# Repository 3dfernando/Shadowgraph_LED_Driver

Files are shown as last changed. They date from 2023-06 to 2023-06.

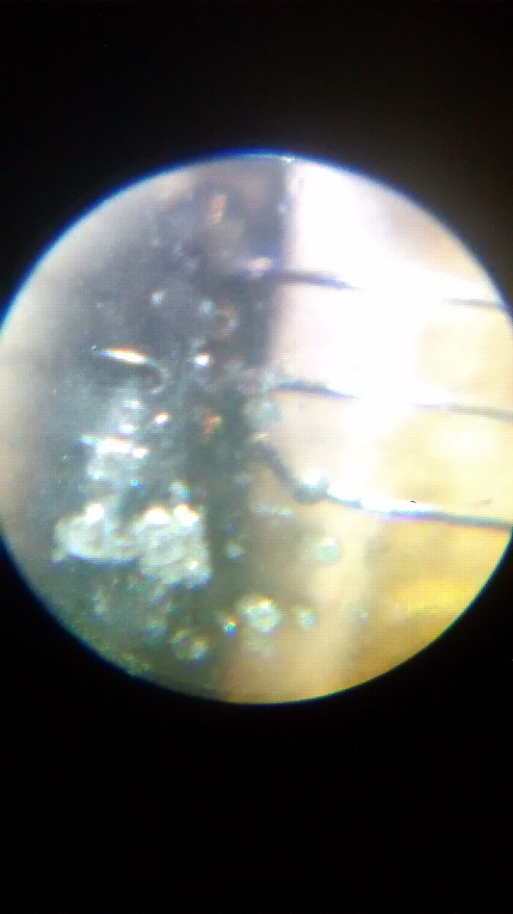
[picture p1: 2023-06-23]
Failure Pictures/IMG_20171130_173702805.jpg

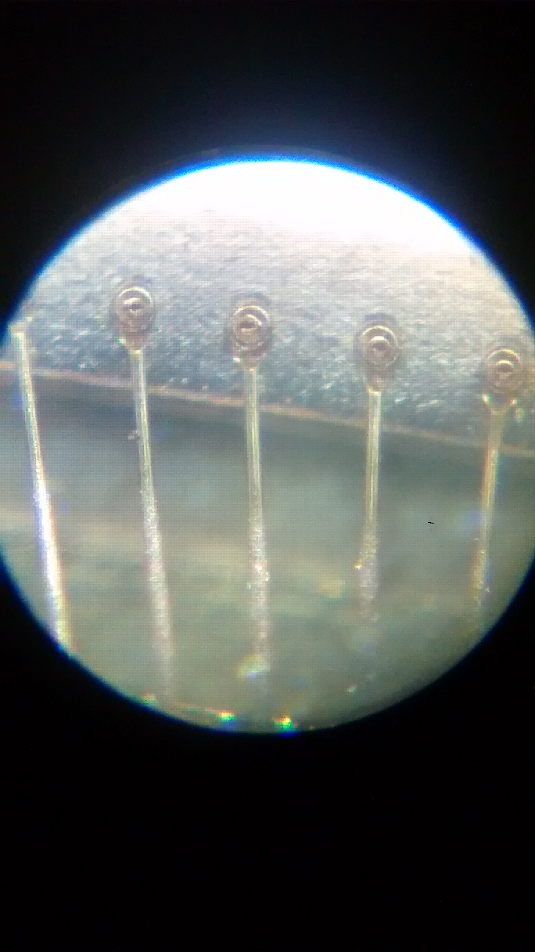
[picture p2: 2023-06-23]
Failure Pictures/IMG_20171130_174007732.jpg

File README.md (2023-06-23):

# Shadowgraph LED Driver
A simple electronic circuit board design for overdriving a pulsed LED flash for shadowgraph purposes. 

*** WARNING: This circuit overdrives an LED with up to 200A of current. COMPONENTS WILL GET BURNED! Be careful in your explorations and make sure you understand the circuit before you start messing with it! ***

# Circuit Description
The circuit schematic, provided in Circuit Diagram.pdf, is very simple. 
24V are provided to a nominally 3.8V LED through a high-power MOSFET (IRF3805) for the duration of the input pulse, which should be very short (order 10us or less) and of very low duty cycle (less than 1% recommended).

The current provided to the LED can reach 200A at full power. 200A will, however, explode the LED bond wires, rendering it useless. Since the LED is very expensive (about $100 as of 2023 for the white LED), it is not recommended to drive at max power. The LED provides a good flash at 100-120A and you should really not exceed 150A (that's where sometimes it may or may not burn depending on other conditions).

There is so much current in such a little time to run the LED that the MOSFET IRF3805 needs a driver IC to provide the inrush current of up to 8A. This obviously cannot be provided by a function generator, which is why the UCC27424 is there to convert the high impedance of the fn. generator to a low impedance required by the MOSFET gate. The UCC27424 can be destroyed if the MOSFET fails. This is because when the MOSFET fails, it can fail such that the Gate and Source terminal are shorted. In this case, the current going through the UCC driver will exceed the 8A rating and burn the IC, so both need to be replaced in this case.

To adjust the amount of current going through the LED, adjust the output voltage of the LM2596 DC-DC converter circuit. This can be done using a small screwdriver to adjust the trimmer-potentiometer in the DC-DC converter. The output voltage will range between 9 and 16V during operation, depending on the amount of current you want for the LED. 

The amount of current running through the LED can be measured with an oscilloscope by watching the voltage drop across the 0.02Ohm resistor. For 100A, for example, we have V=I*R=100A * 0.02Ohm = 2V across the resistor. Since the LED is expensive, you can connect a piece of short wire between the LED terminal connectors (i.e., generate a short circuit), in order to test the system. Once you are confident the current is about 100A or so, connect the LED and test your optics to see if the brightness is sufficient. If it isn't, you can increase the power by using the trimmer-potentiometer in the DC-DC converter, bearing in mind that at about 150A the LED, MOSFET and UCC driver will be destroyed.

Note: The LED has a small thermal mass and will heat up rather quickly if you use a high duty cycle for this driver. The average power dissipation of the LED can exceed 1200W with 1% duty cycle, meaning you will not be able to build a heat sink with acceptable specs for the LED. Best is to simply bolt the LED to a large aluminium block to provide it with thermal mass, and just not run it for too long. The LED may fail over a few minutes if it overheats.

# How to make this
1. First, download Gerbers.zip and send the Gerber files to a PCB manufacturer company.
2. Assemble the PCB according to Circuit Diagram.pdf. Make sure all components are oriented correctly! The bill of materials is provided in BOM.xlsx
3. There is an Operation Instructions.pptx file with directions and pictures on how the PCB looks like. The terminal blocks and DIP8 socket enable replacement of the components that are likely to be damaged if you don't know what you are doing. Make sure you buy extra transistors IRF3805 and UCC27424P chips, as they really can burn very easily until you understand the limitations of this device. 
4. Start testing the board, according to the instructions and warnings in "Circuit Description". Have spare parts - you will need them!

# Known operation conditions
This circuit has been successfully operated at conditions listed below:
* 500Hz, 10us pulse width, indefinitely;
* 500kHz, 0.5us pulse width, for 2-3 seconds (Pulse burst mode in a function generator);
* 10-50kHz, 1us pulse width, for ~30 seconds;
* Minimum pulse width to get any meaningful amount of light is about 100ns (See Pictures/Photodiode measurements folder);
* This circuit is not designed to operate without pulsing (i.e., continuously). Likely all components will fail due to the extremely high currents.

As you can see, this is a very tricky circuit to work with. It provides some real juice for your shadowgraphs, allowing for imaging at very high frame rates. Have fun building it!

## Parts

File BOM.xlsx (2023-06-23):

Item | Qty | Cost/ea | Total Cost | Link
1. Electronic Driver Board |  |  | $22.25
LM2596 Buck Converter, DC to DC | 1 | $1.33 | $1.33 | https://www.amazon.com/LM2596-Converter-3-0-40V-1-5-35V-Supply/dp/B0B3M91PNJ/ref=sr_1_4
UCC27424P | 1 | $1.61 | $1.61 | https://www.digikey.com/en/products/detail/texas-instruments/UCC27424P/603254
RES 22K | 2 | $0.10 | $0.20 | https://www.digikey.com/en/products/detail/yageo/CFR-12JB-52-22K/3966
RES 1.5OHM | 1 | $0.42 | $0.42 | https://www.digikey.com/en/products/detail/te-connectivity-passive-product/RR03J1R5TB/9371815
BNC CONNECTOR | 1 | $1.94 | $1.94 | https://www.digikey.com/en/products/detail/molex/0731000105/1465146
IRF3805 | 1 | $4.15 | $4.15 | https://www.digikey.com/en/products/detail/infineon-technologies/AUIRF3805/2605469
RES 0.02OHM | 1 | $0.97 | $0.97 | https://www.digikey.com/en/products/detail/riedon/MSR3-0R02F1/1641078
TERM BLK 3POS TOP ENT 5.08MM PCB | 1 | $1.86 | $1.86 | https://www.digikey.com/en/products/detail/te-connectivity-amp-connectors/282851-3/1136743
MACHINED DIP 8 SOCKET | 1 | $0.50 | $0.50 | https://www.digikey.com/en/products/detail/mill-max-manufacturing-corp/110-99-308-41-001000/32045
TERMINAL BLOCK 2 POS, SCREW TYPE, 5.08 | 3 | $0.77 | $2.31 | https://www.digikey.com/en/products/detail/cui-devices/TB004-508-02BE/10064103
1uF CAP | 1 | $1.93 | $1.93 | https://www.digikey.com/en/products/detail/avx-corporation/SR215C105KAR/7536274
330uF CAP | 1 | $0.69 | $0.69 | https://www.digikey.com/en/products/detail/illinois-capacitor/337CKS050M/5412323
Power Connector PCB Male | 1 | $0.96 | $0.96 | https://www.digikey.com/en/products/detail/w%C3%BCrth-elektronik/694108301002/5047524
Power Connector Cable Female | 1 | $1.66 | $1.66 | https://www.digikey.com/en/products/detail/cui-devices/PP3-002BH/2197312
THT Connector Female | 4 | $0.43 | $1.72 | https://www.digikey.com/en/products/detail/mill-max-manufacturing-corp/801-47-001-10-001000/7364070
2. LEDs |  |  | $98.45
White LED for Shadowgraph (CBT-140-WCS-L16-UA120) | 1 | $98.45 | $98.45 | https://www.digikey.com/en/products/detail/luminus-devices-inc/CBT-140-WCS-L16-UA120/5247636
Blue LED 405nm for PSP (CBM-120-UV-X31-L400-22) | 1 | $353.36 | $353.36 | https://www.digikey.com/en/products/detail/luminus-devices-inc/CBM-120-UV-X31-L400-22/9681349
UV LED 368nm, alternative for PSP (CBM-120-UV-X31-I365-22) | 1 | $450.89 | $450.89 | https://www.digikey.com/en/products/detail/luminus-devices-inc/CBM-120-UV-X31-I365-22/9749620
 |  |  | $0.00
 |  |  | $0.00
 |  |  | $0.00
 |  |  | $0.00
 |  |  | $0.00
 |  |  | $0.00
Total Cost |  |  | $120.70

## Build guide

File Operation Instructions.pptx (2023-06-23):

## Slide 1

Provide input waveform
in this BNC
(5V=on, will switch on for as long as pulse is active)
Typical pulse width 500ns to 5us

+24V input voltage here
(up to 3A)
Can use a power supply rated for less current if known avg current is lower

DIP8 Socket for UCC27424P
(If not operated within specs this component burns, socket is for easy replacement)

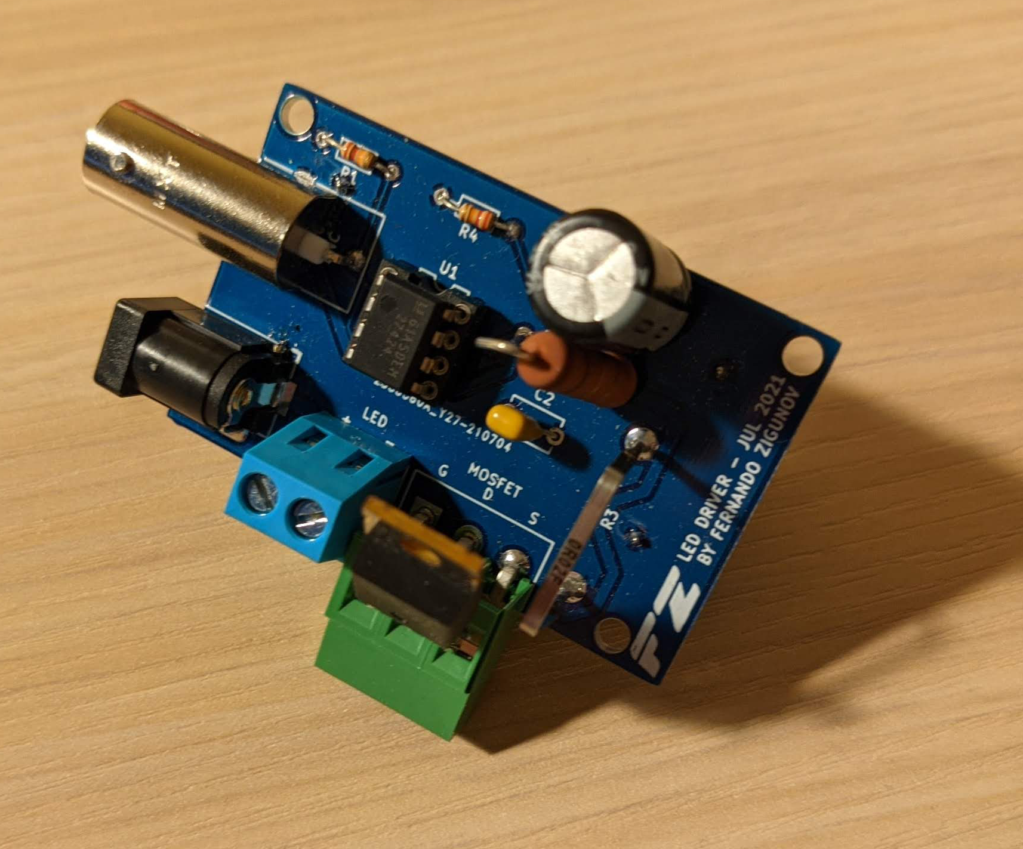
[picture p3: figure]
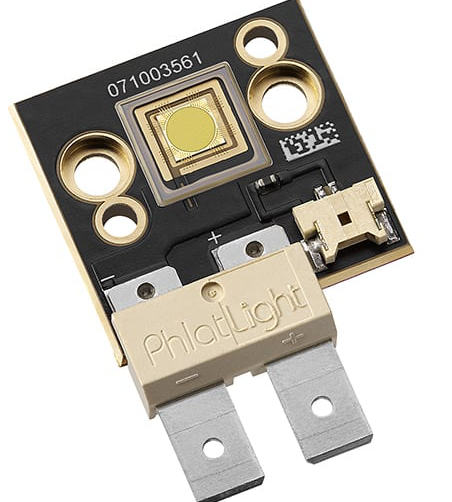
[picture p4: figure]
CBT-140 Series

Terminals to LED
(make wires as short as possible for fast switching)

Screw terminal for IRF3805 MOSFET
(If not operated within specs this component burns, so this is for easy replacement)
G=GATE, D=DRAIN, S=SOURCE
DON’T CONNECT INCORRECTLY!!
Black plastic body must be facing outward

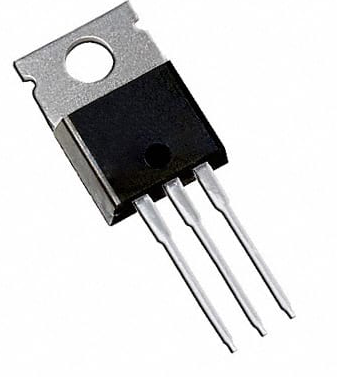
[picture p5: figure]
TO-220AB PKG

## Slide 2

LM2596 based Boost Converter
- Solder header pin terminals for easy connection to the main PCB
- (MAKE SURE TO CONNECT IT IN THE RIGHT ORIENTATION!)

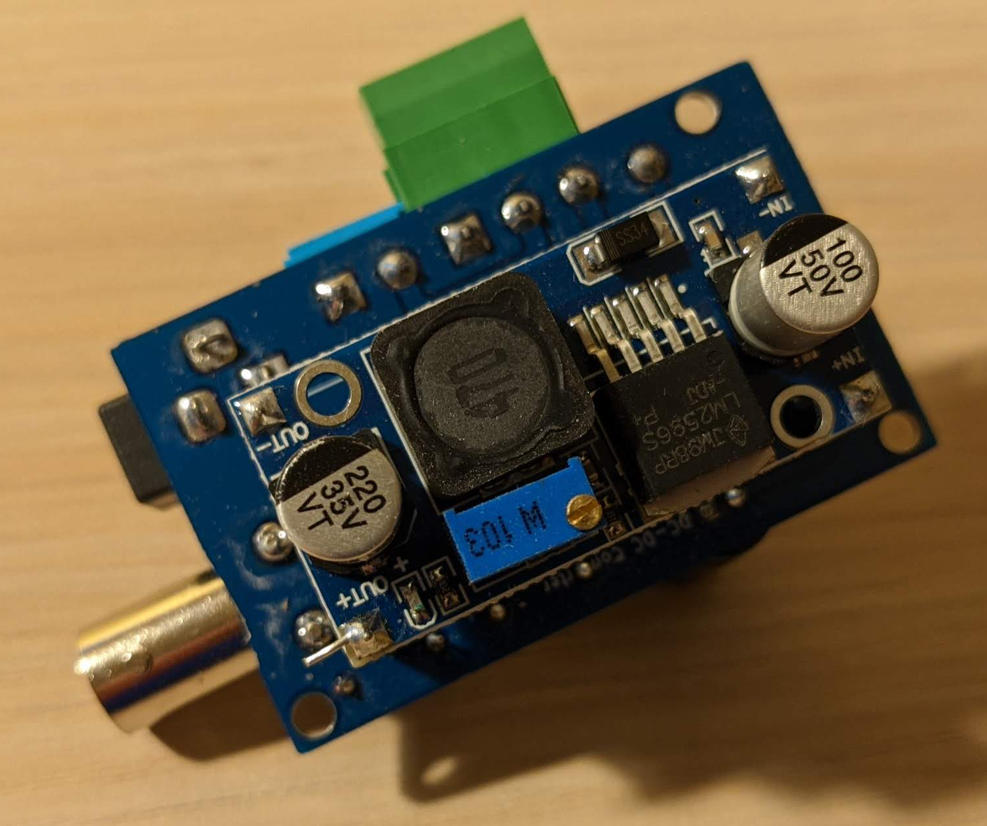
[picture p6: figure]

Once LED is connected you can connect an oscilloscope to this resistor to measure the current going to the LED. (Use Ohm’s law)
DO NOT EXCEED 150A! It will burn the LED!
If unsure, you can connect a short-circuit wire to the LED terminals to measure the current before connecting the LED.

Voltage output adjustment screw
Start with ~8V before connecting LED.

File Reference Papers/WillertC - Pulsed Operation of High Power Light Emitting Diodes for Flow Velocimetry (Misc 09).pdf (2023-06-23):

8TH INTERNATIONAL SYMPOSIUM ON PARTICLE IMAGE VELOCIMETRY - PIV09
Melbourne, Victoria, Australia, August 25-28, 2009

## Pulsed Operation of High Power Light Emitting Diodes for Flow Velocimetry

C. Willert¹

, S. Moessner¹ and J. Klinner¹

1Engine Measurement Techniques, Institute of Propulsion Technology, German Aerospace Center (DLR), 51170 Koln, GERMANY ¨ chris.willert@dlr.de

ABSTRACT

High powered light emitting diodes (LED) are investigated for possible uses as light sources in flow diagnostics, in particular, as an alternative to laser-based illumination in particle imaging flow velocimetry. Recent developments in solid state illumination resulted in mass-produced LEDs that provide average radiant power in excess of 10 Watt. By operating these LEDs with short duration, pulsed currents that are considerably beyond their continuous current damage threshold, light pulses can be generated that are sufficient to the illuminate and image micron sized particles in flow velocimetry. kilohertz frame rate PIV measurements in water are presented. The feasibility of LED-based PIV measurements in air is also demonstrated.

LIST OF SYMOBLS

Alum | emitter luminescent area
N.A. | numerical aperture
If,cw | nominal continuous forward current
If,max | maximum continuous forward current
λo | dominant emission wavelength
Φv | luminous flux in lumen (lm)
Φr | radiometric flux in Watt (W)
τ | pulse delay

### 1. INTRODUCTION

While earlier generations of LEDs were primarily used as indicators in every-day electronics, recent developments have resulted in mass-produced devices whose light output rivals that of conventional light sources such as incandescent light bulbs and now find an increased range of applications ranging from architectural lighting to projection system and automotive head lights. In the framework of flow diagnostics LEDs promise a number of attractive advantages in comparison to lasers and therefore deserve closer investigation. Aside from the dramatically reduced cost of procurement and considerably longer life time, a LED provides incoherent light over a rather wide wavelength range (typ. ±10 − 30 nm) which alleviates many issues related to speckle artifacts found in laser based illumination. If operated in pulsed mode, the luminosity signal of a LED is extremely stable, both in terms of intensity as well as spatial intensity distribution.

Another interesting characteristic and a main point of emphasis of the present work, is that LEDs can be operated significantly beyond their damage threshold using high current, short duration pulses. In this case, the temperature within the substrate (junction temperature) stays below the damage threshold while the photon generation per time-unit is approximately increased in proportion to the current increase [1, 2]. This makes the LED particular interesting for utilization as a pulsed light source in image based diagnostics. The literature reports the use of LEDs in Schlieren imaging [3], bubble shadowgraphy [4, 5, 6], shadow velocimetry [7], PIV
[8] as well as micro-PIV [9]. If operated in a forward scatter shadowgraphy arrangement short duration pulses below 250 ns enable high-speed shadowgraphy in the 100 kHz range of kerosene sprays at high magnification [10]. The present work focusses on side-scatter illumination geometries commonly used in PIV and PTV which requires significantly higher illumination intensities.

### 2. OVERVIEW OF HIGH CURRENT LEDS

Table 1 lists the characteristics of several representative LEDs tested in the course of the feasibility study. Mainly green LEDs were investigated, in part, because present day imaging sensors exhibit peak quantum efficiencies in the yellow/green range (550 − 530 nm), similar to the response of the human eye. The listed devices represent two different types of LEDs: The first three, available from Philips Lumileds, are designed for general illumination purposes and contain rather small luminous emission chips which are encapsulated in a lens shaped clear dome. The other two devices, available from Luminus Devices Inc., are specifically designed for projection systems. Here the luminescent substrate is covered by a thin glass window similar to an imaging sensor. Contrary to most commonly available LEDs these devices are essentially surface emitters with a nearly constant intensity distribution per unit area. This is achieved by a photonic lattice bonded to the surface of the emitter which channels the light through micron-sized, surface-normal holes. Because of this, the radiation pattern is more bundled than for conventional high-current LEDs.

Emitter | If,cw (A) | ΦV (lm) | λo (nm) | If,max (A) | Alum (mm² )
LXHL-PD09 LXHL-PL09 LXHL-PM02 CBT40 CBT120 | 1.4 1.4 0.7 5.9 18 | 140 110 160 625 2100 | 627 590 530 528 528 | 1.54 1.54 1.00 12 36 | ≈ 1.5×1.5 ≈ 1.5×1.5 ≈ 2×2 2.09×1.87 4.6×2.6

Table 1: Specifications of selected high-current LEDs

### 3. LED CHARACTERISTICS IN PULSED OPERATION

Figure 1 illustrates the increased luminosity of two high power LEDs that are driven with short-duration current pulses (here 1µs at 1 kHz). In both cases the LEDs are driven up to maximum currents in the 30A range which is more than a factor 20 higher than the rated current If

| for red LED. For
the green LED the rated current is exceeded by a factor of 5 suggesting further increase without damage to the device. In fact none of the tested devices suffered any noticeable damage when operated in pulsed mode at these current levels and low

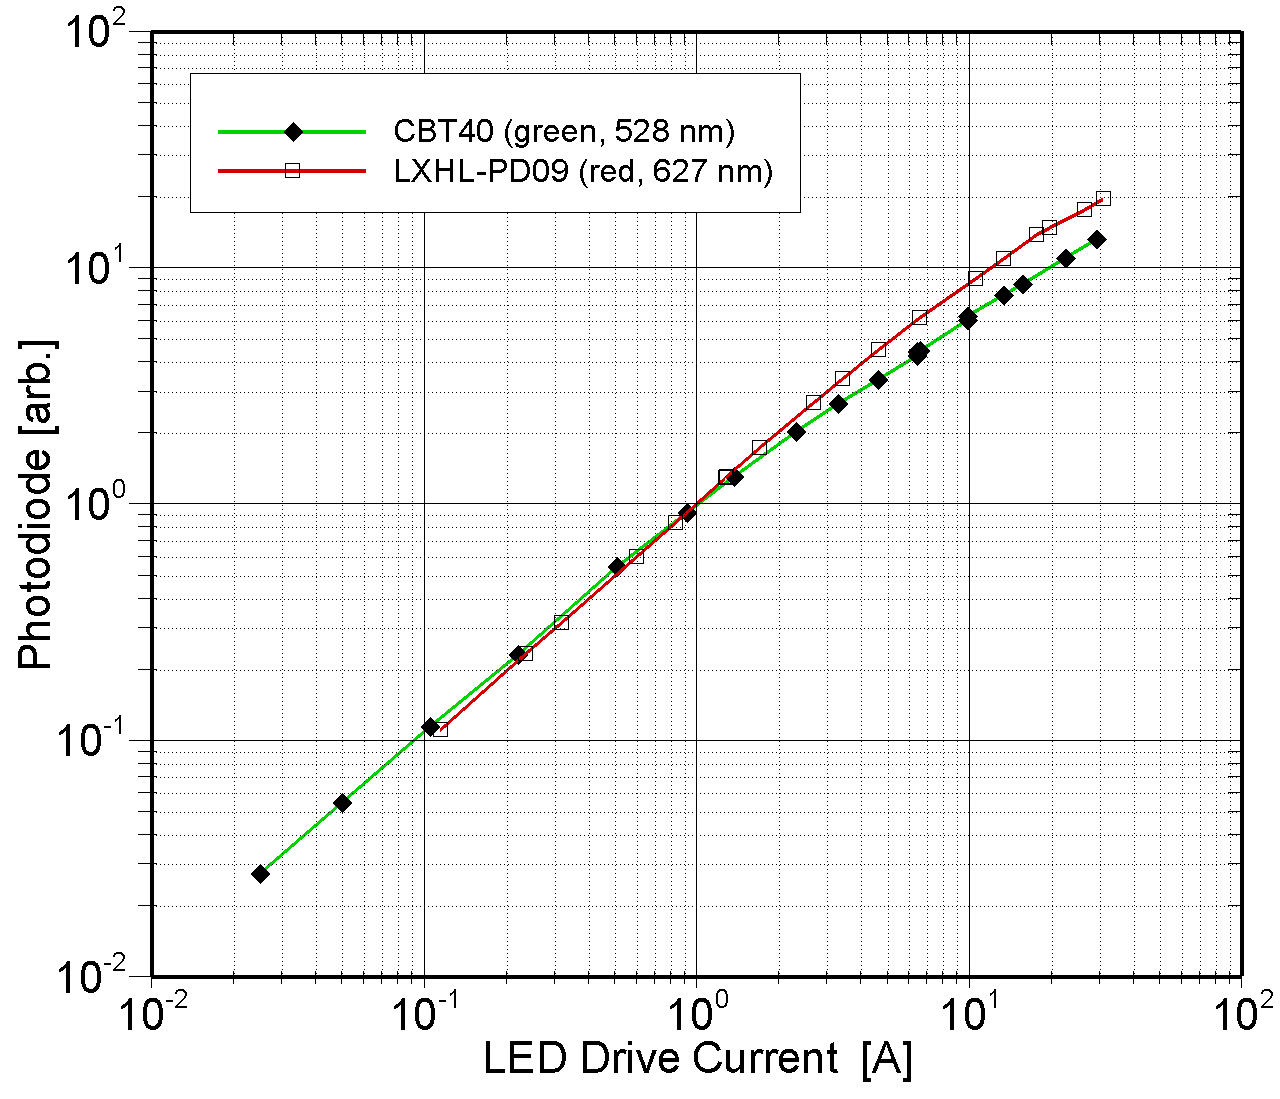
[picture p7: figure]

Figure 1: Luminosity of high power LEDs driven with 1µs current pulses

duty cycle (less than 1 : 100).

The data shown in figure 1 confirms the known increase of luminous flux Φv with an increasing drive current If
. For
the red LED the increase of current leads to a proportional increase for low drive currents. At higher currents the efficiency factor or proportionality reduces to about 0.4. The green LED (CBT-40) exhibits a similar behavior for low currents but decreases to about 0.35 at currents beyond 10A. This indicates a decreasing proportionality with increasing drive currents due to saturation effects. Not shown is data for the 5W green LED (LXHL-PM02) for which the proportionality decreases to 20% at currents beyond 30A. In comparison the high power device CBT-120, which has a 3 times larger luminescent area than the CBT-40, exhibits an proportionality of 40% at 40A, indicating considerable margins for operation at even higher currents.

Measurements of the type shown in figure 1 allow an approximate extrapolation of luminous flux (or effective pulse energy) at even higher currents. The smaller high current devices LXHL-PD09 (red) and LXHL-PM02 (green) could be driven at pulsed currents of 50A without immediate damage, exceeding the rated current by a factor of 30 and 70, respectively. This suggests that the stronger devices CBT-40 and CBT-120 can be driven at significantly higher currents in the 100−200A range. The data sheet for the CBT-120 quotes a radiometric flux Φr = 6.3W (Φv = 3100lm) when driven at a pulsed current of If = 30A at 240Hz and a 50% duty cycle [11]. The effective pulse power then is Φr = 12.6W for the duration of the current pulse. Assuming a conservative proportionality of 35% light output increase with respect to increasing current – as indicated in figure 1 – this would result in an effective pulse power of close 60W at If = 200A drive current. This corresponds to a pulse energy of 60µJ for a 1µs pulse. As will be shown later this is sufficient to perform reliable high-speed PIV measurements in water.

A side effect of the pulsed operation of LEDs is that the emission wavelength may shift considerably as the current is increased. This effect is shown in figure 2 for two LED emitters. The drive pulses are approximately chosen to be of similar integral input power to maintain an average junction temperature. While the amber LED (LXHL-PL09) shows only a minor frequency shift of about ∆λ = 2 nm toward longer wavelengths, the green device shifts by more than ∆λ =

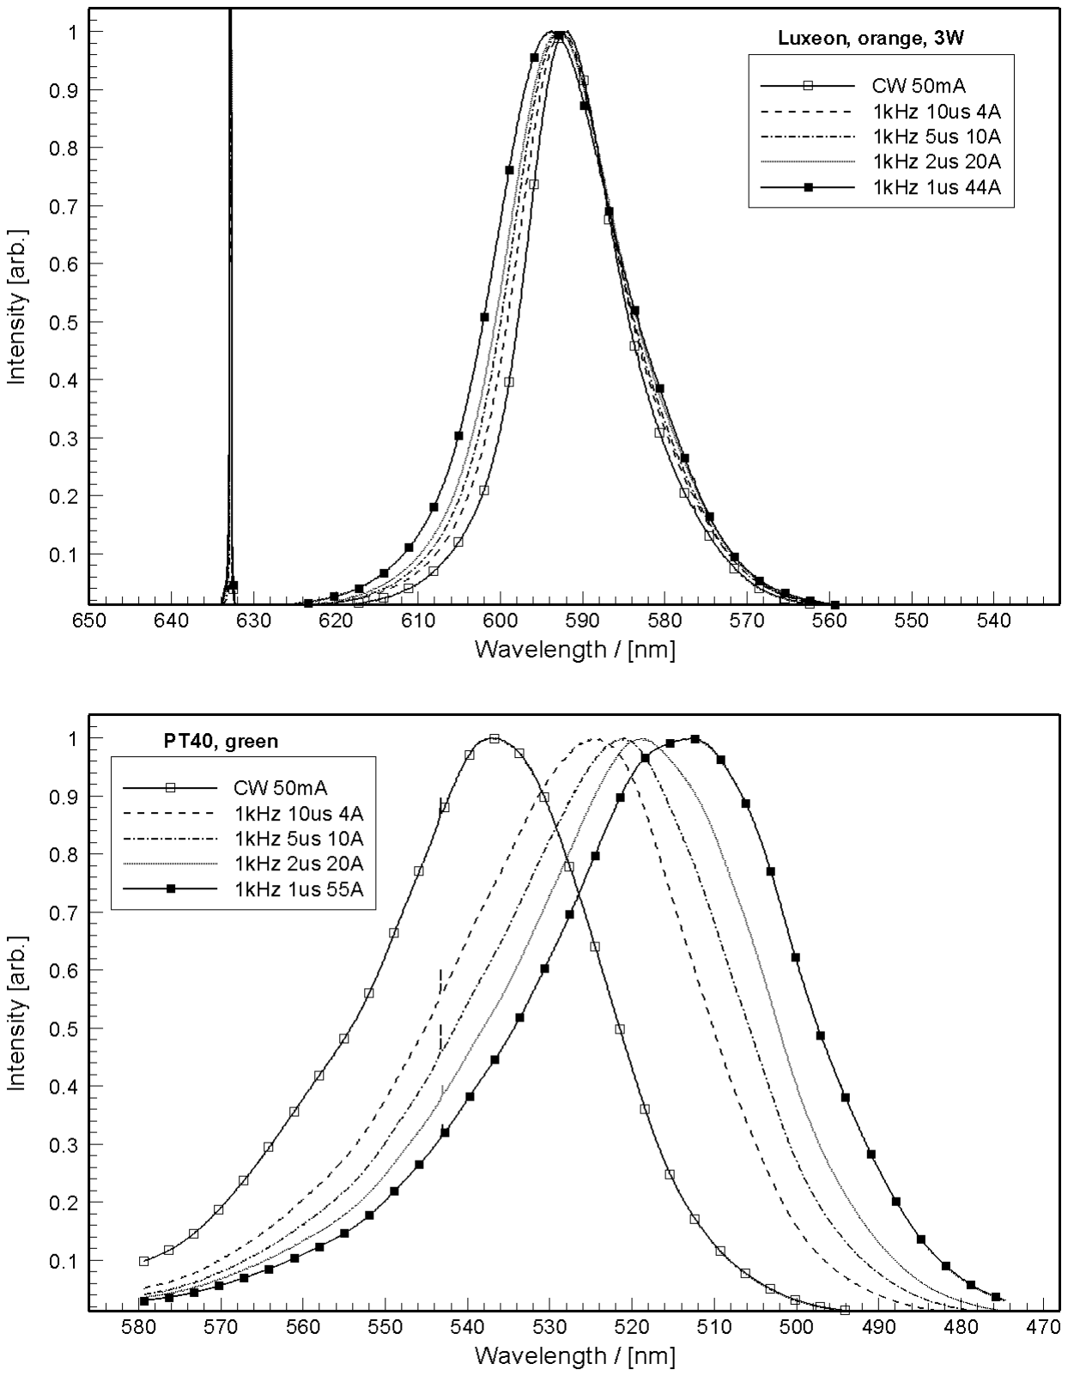
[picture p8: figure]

Figure 2: Spectral intensity distribution of LEDs operating in continuous and pulse modes. Top: LXHL-PL09 (amber); bottom: CBT-40 (green)

30 nm toward a cyan color. The effect is characteristic for the respective junction materials that the devices are made of: typically GaAsP or AlInGaP for the red and orange luminescence and InGaN for the green and blue LEDs [12]. The spectral width increases slightly for both devices as the drive current increases. In general green device has a much wider emission spectrum which is also attributed to the junction material (so called alloy broadening [12]). While the frequency shift may not be a issue for many velocimetry applications it nonetheless may be of interest when color-selective cameras and filters are used.

While none of the devices were damaged due to current over-driving, increased aging will occur resulting in a gradual reduction of light emission, but this has not been investigated by the authors. Driving the LEDs at high currents briefly increases the junction temperature which strains the crystal causing defects in its lattice which then no longer contribute to light generation.

### 4. PIV USING LED

As mentioned in the introduction, the literature reports a number of earlier PIV applications involving LED clusters as light sources [4, 8, 7, 9, 5]. In these applications the LEDs were rarely overdriven to levels reported here and generally operated in a in-line imaging arrangement or relied on large particles to achieve sufficient light scattering.

The present LED-PIV investigations focussed on using single LEDs to illuminate particles in side-scatter which is commonly used in planar PIV. Initially volume illumination was used in which the luminescent area of the LED is projected into the flow under investigation using condenser lenses. A combination high magnification and large lens aperture limited the depth of field

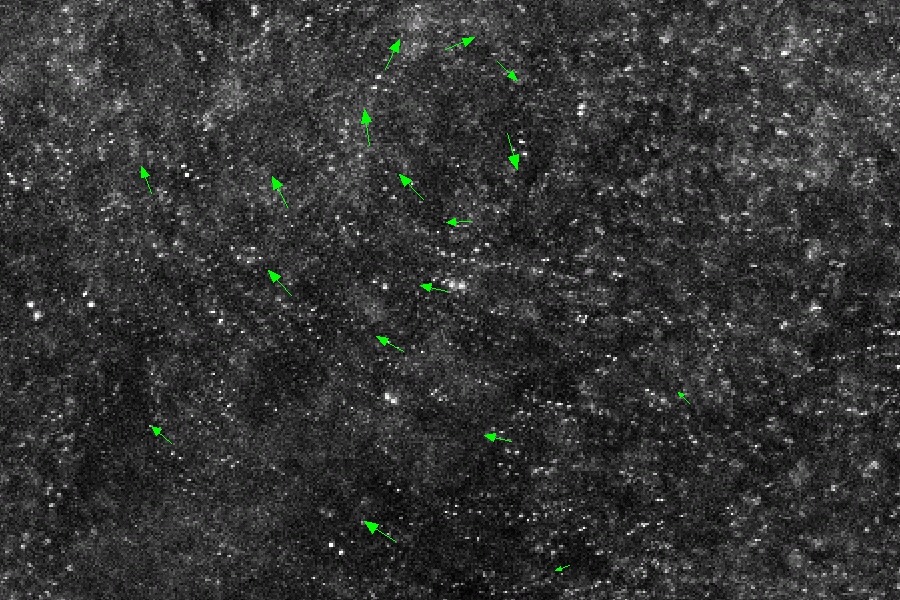
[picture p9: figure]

Figure 3: Portion of high magnification PIV recording obtained with LED illumination in forward scatter. A mean horizontal displacement of 14 pixels is subtracted

in the sub-millimeter regime and permitted two-component PIV measurements on an area of about 9 × 7mm²
. A 5W-class
green LED (LXHL-PM02) was pulsed at If = 2A for 20µs. PIV measurements were reliable using 10µm particles in water, imaged by a cooled, double-shutter CCD camera.

Later PIV experiments made use of stronger, projection type LEDs (CBT-40, CBT-120) that could be driven at much higher currents. Figure 3 shows a 3×2mm² portion of a PIV recording obtained in a free jet in air seeded with 1 − 3µm glycerine droplets. Volume illumination was provided by the CBT-120 LED device using 30A pulses of 2µs duration. The pulse delay was τ = 15µs. Arranged in a 45◦
forward scattering with respect to the LED light a macro lens (Nikon Nikkor MF 55mm/f2.8) with aperture set at f]4 imaged the flow onto the actively cooled sensor (1376 × 1040 pixel) of a double-shutter CCD camera (PCO Sensicam QE) using a magnification of approximately 1:1. Assuming a circle of confusion of 5 pixel the depth of field is estimated to be 500µm. The processed PIV data set shown in figure 4 was analyzed using sampling areas of 48×48 pixel (320×320µm²
).

While these PIV measurements demonstrate the feasibility of imaging micron-sized droplets in air at moderate velocities using rather short illumination pulses, the method of volume illumination has the drawback of introducing significant background signal due to the light scattered by out-of-focus particles. This reduces image contrast and poses a general problem for micro-PIV applications. Therefore possibilities of converting the highly divergent light of the LEDs into a light sheet were investigated in a next iteration.

The most promising experiments were performed when the LED light was bundled into a light sheet by means of a fiber-optic illumination system, also known as line light. As illustrated in figure 5 the entry side of the fiber bundle is round while the fibers are arranged along a line at the distal end. This line is collimated to form a light sheet using a short focal length cylindrical lens.

Figure 6 provides sample PIV results from a time series of a propeller flow in water acquired at a frame rate of 1.5 kHz using pulsed LED-illumination and a high-speed CMOS camera (Photron, APX-RS, with Nikon Nikkor MF 55mm/f2.8 lens). The water was seeded with 10µm hollow glass spheres. The light sheet thickness was approximately 1 mm a the waist widening to about 2 mm at the edges of the 55mm wide imaged area. Current pulses of 16A and 20µs duration were used. Based on figure 6 the pulse duration could have been reduced to

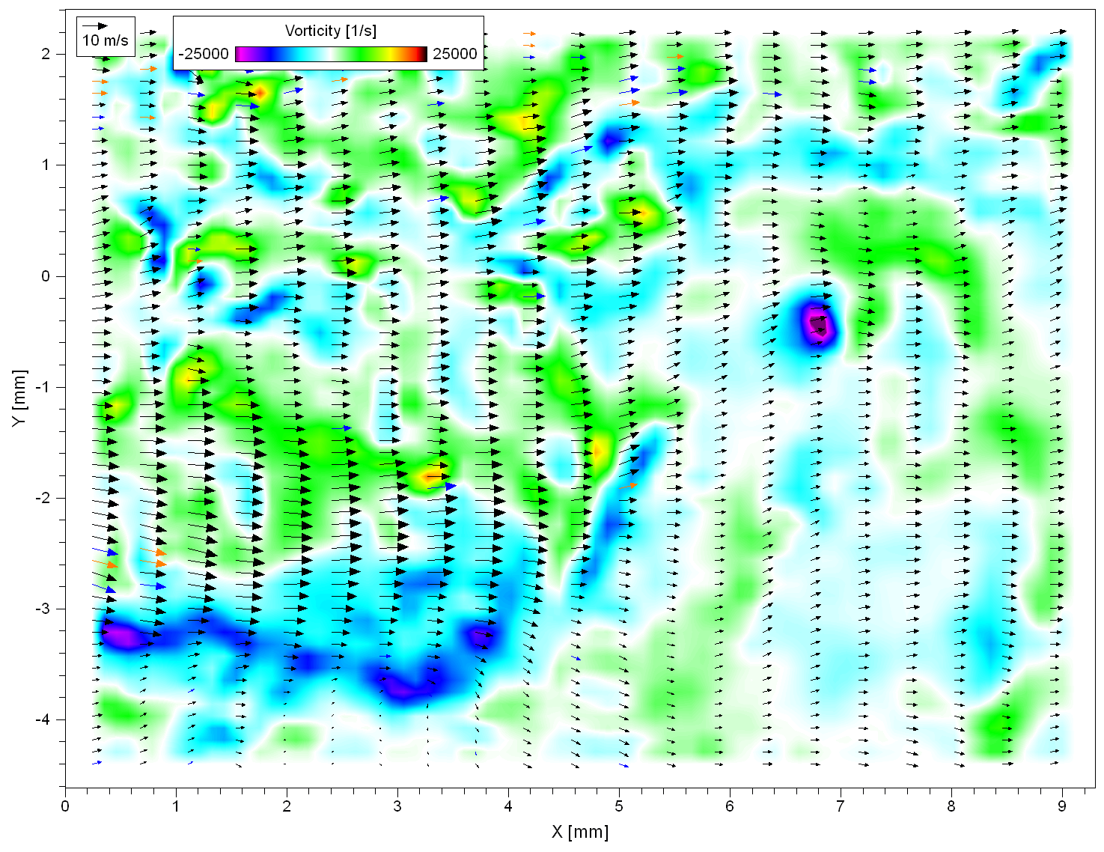
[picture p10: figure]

Figure 4: Processed PIV data set corresponding to figure 3 obtained with LED illumination. Horizontally only every fourth velocity vector is shown; orange vectors indicate interpolated data

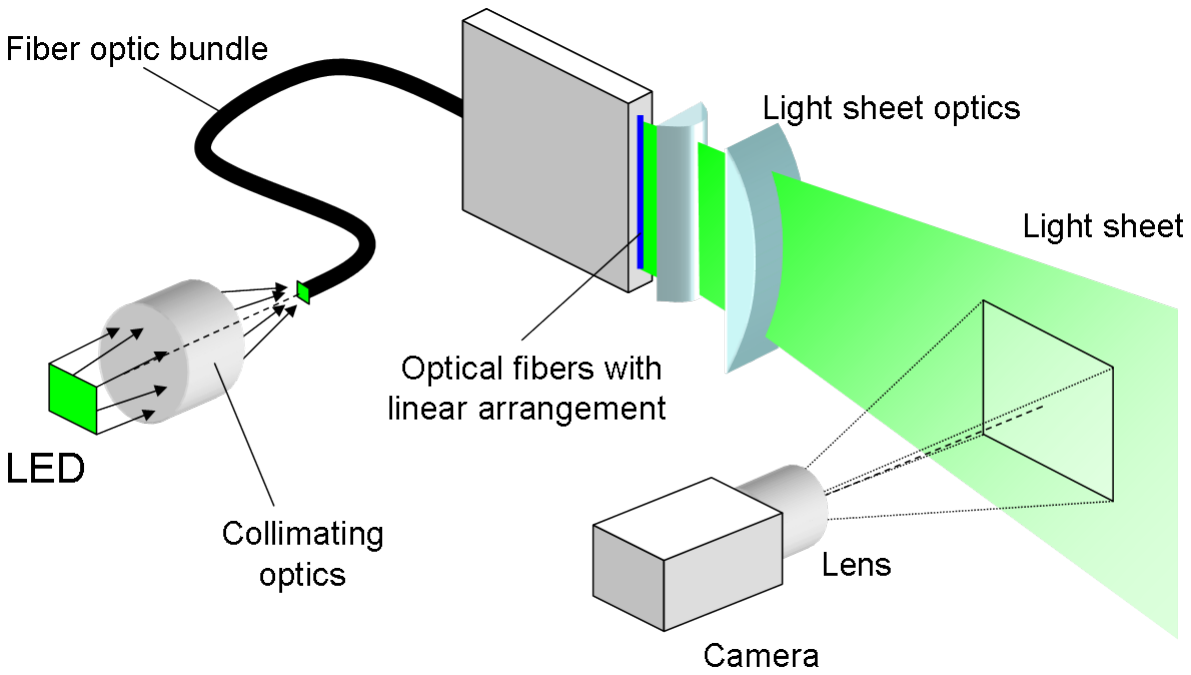
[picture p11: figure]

Figure 5: LED-based light sheet illumination using fiber optic assembly

10µs using pulses of 40A (A suitable high current source was not available at the time of the experiment).

Prior to PIV processing the recorded images were subjected to image enhancement involving background subtraction and minor blurring to reduce spurious noise. The particle image density was sufficient to sample the image with 16 × 16 pixel sub-windows, corresponding to 0.84×0.84mm²

### 5. DISCUSSION

The previously described experiments clearly demonstrate the viability of using pulsed, high power LEDs as illumination sources for PIV. Generally being a non-collimated light source is one the more critical drawbacks of the LED. This makes it difficult to establish light sheet illumination commonly found in macroscopic PIV applications unless additional optics such as the fiber optic line lights are used. Unfortunately the large aperture of the LEDs (N.A. ≈ 0.22) does not match well to the smaller aperture of optical fibers (typ. N.A. = 0.22), such that a significant amount of light is lost. Comparable measurements between volume illumination and light sheet illumination indicated that about three quarters of the light is lost by the fiber transmission system.

On the other hand it is viable for LEDs to provide volume illumination for microscopic PIV or photogrammetric particle imaging methods such as tomographic PIV or 3-D particle tracking. In comparison to most pulsed lasers the light pulses can be ‘fired’ nearly immediately. There is no lead time as

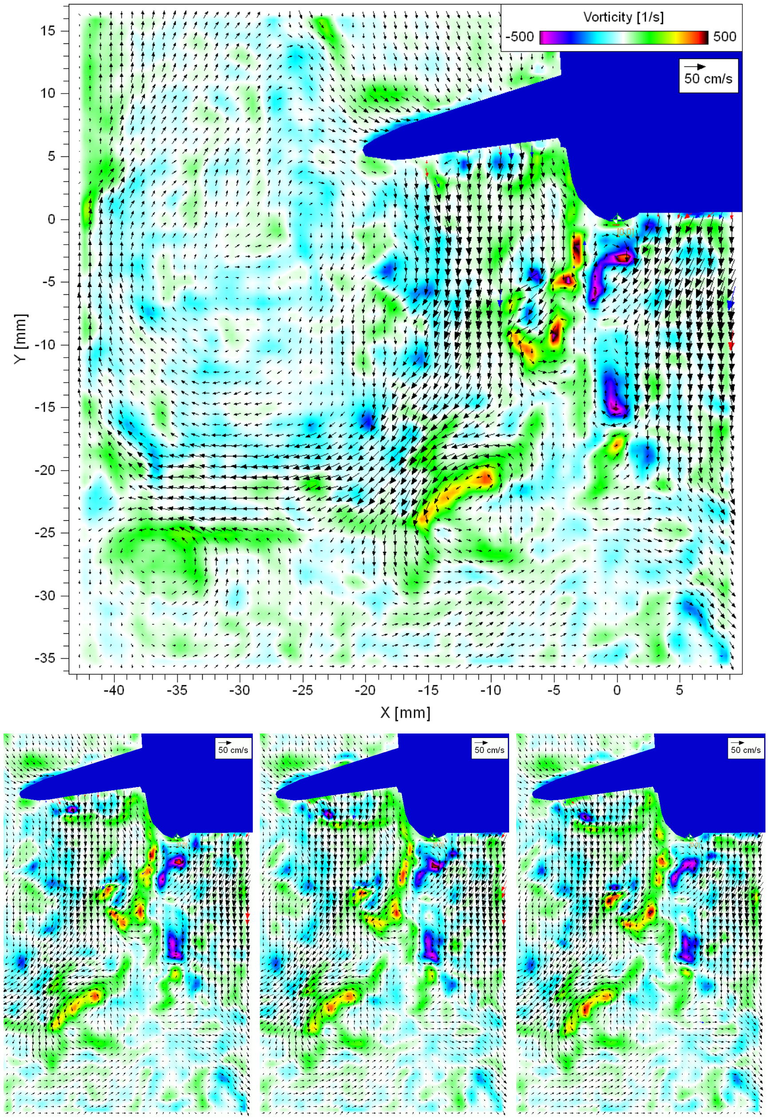
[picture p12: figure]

Figure 6: Four consecutive PIV maps from a time-resolved image sequence acquired at 1.5 kHz for a propeller flow inside a small water tank. Separation between displayed recordings is 1.33ms. For better visibility only one fourth of the vectors are displayed

with lasers to ‘pump’ the lasing medium. Also the repetition rate can be freely varied since it is not necessary to adhere to fundamental pulsing frequencies. Pulse-to-pulse intensity and spatial variations are practically not present. The broad spectral intensity distribution of the LED’s electroluminescence prevents the creation of speckle (interference of coherent light). From a handling point of view the un-collimated light of LEDs is less dangerous, but not necessarily eye-safe, while supply voltages are considerably lower than for pulsed lasers.

### 6. CONCLUSIONS

The use of LED based illumination for flow measurement was investigated on the background of a possible alternative to commonly used laser based illumination. The study was motivated by the recent availability of high power LEDs with continuous radiant flux levels comparable to that of lasers. Pulsed light at significant intensity levels can be obtained from these solid state devices by briefly overdriving them with high currents. This permits PIV measurements in both water and air.

Challenges yet to be solved are associated with the rather wide-angle radiation pattern (i.e. high N.A.) of the light issuing from the luminous surface of the LED. The high numerical aperture restricts the creation of thin light sheets comparable to those achieved with the collimated light of lasers. Nonetheless reasonable light sheets could be achieved using a fiber optic collimating device with which time resolved PIV measurements were performed in water at frame rates exceeding 4 kHz (not presented here).

Currently available high power LEDs are particularly well suited for applications requiring volume illumination such as shadowgraphy or even the recently introduced volume resolving, particle based velocimetry techniques (e.g. tomographic PIV or 3D-PTV). PIV systems using LEDs as light sources can be assembled at significantly reduced costs. Compact, battery operated systems are feasible and could be of interest for in-flight measurements or autonomous operation in hazardous environments.

ACKNOWLEDGMENTS

This work was funded in part by the German Ministry of Education and Research (BMBF), PTJ Research Project number 03FPE00003. This support is gratefully acknowledged by the authors.

REFERENCES

[1] Hiller W, Lent H M, Meier G E A, Stasicki B (1987): A pulsed light generator for high speed photography, Experiments in Fluids, 5(2):141–144.
[2] Stasicki B, Hiller W, Meier G E A (1984): Hochfrequenz-Stroboskop mit LED-Lichtquelle, Tech. Messen, 51:217–220.
[3] Buttsworth D, Ahfock T L (2003): A pulsed LED system for Schlieren flow visualization, Tech. Rep. TR-2003-01, Faculty of Engineering & Surveying, Univ.
S. Queensland, Australia.
[4] Broder D, Sommerfeld M (2007): Planar shadow ¨ image velocimetry for the analysis of the hydrodynamics in bubbly flows, Measurement Science & Technology, 18:2513–2528.
[5] Lindken R, Merzkirch W (2002): A novel PIV technique for measurements in multiphase flows and its application to two-phase bubbly flows, Experiments in Fluids, 33(6):814–825.
[6] Nogueira S, Sousa R, Pinto A, Riethmuller M, Campos J (2003): Simultaneous PIV and pulsed shadow technique in slug flow: a solution for optical problems, Experiments in Fluids, 35(6):598–609.
[7] Estevadeordal J, Goss L, PIV with LED: Particle Shadow Velocimetry (PSV) Technique, in: 43rd AIAA Aerospace Sciences Meeting and Exhibit (Reno, Nevada, 2005).
[8] Chetelat O, Kim K C (2002): Miniature particle ´ image velocimetry system with LED in-line illumination, Measurement Science and Technology, 13(7):1006–1013.
[9] Hagsater S M, Westergaard C H, Bruus H, Kutter J P ¨ (2003): Investigations on LED illumination for micro-PIV including a novel front-lit configuration, Experiments in Fluids, 44(2):211–219.
[10] Willert C, Freitag S, Hassa C, High speed imaging of fuel sprays using a low-cost illumination source, in: 22nd European Conference on Liquid Atomization and Spray Systems (ILASS 2008) (2008).
[11] Luminus Devices I (2008): Technical product data sheet PDS-001226: CBT-120 Series, PhlatLight LED Illumination Products.
[12] Saleh B, Teich M, Fundamental of Photonics (John Wiley & Sons, Hoboken New Jersey, 2007), 2 edn., ISBN 978-0-471-35832-9.

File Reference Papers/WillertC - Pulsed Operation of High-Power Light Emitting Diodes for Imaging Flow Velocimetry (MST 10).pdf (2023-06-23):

IOP PUBLISHING | MEASUREMENT SCIENCE AND TECHNOLOGY
Meas. Sci. Technol. 21 (2010) 075402 (11pp) | doi:10.1088/0957-0233/21/7/075402 (http://dx.doi.org/10.1088/0957-0233/21/7/075402)

# Pulsed operation of high-power light emitting diodes for imaging flow velocimetry

### C Willert¹, B Stasicki², J Klinner¹ and S Moessner¹

1 Engine Measurement Techniques, Institute of Propulsion Technology, German Aerospace Center (DLR), 51170 Koln, Germany ¨ 2 Experimental Techniques, Institute of Aerodynamics and Flow Technology, German Aerospace Center

(DLR), 37073 Gottingen, Germany ¨
E-mail: chris.willert@dlr.de

Received 8 January 2010, in final form 16 April 2010 Published 8 June 2010
Online at stacks.iop.org/MST/21/075402

Abstract
High-powered light emitting diodes (LED) are investigated for possible uses as light sources in flow diagnostics, in particular, as an alternative to laser-based illumination in particle imaging flow velocimetry in side-scatter imaging arrangements. Recent developments in solid state illumination resulted in mass-produced LEDs that provide average radiant power in excess of 10 W. By operating these LEDs with short duration, pulsed currents that are considerably beyond their continuous current damage threshold, light pulses can be generated that are sufficient to illuminate and image micron-sized particles in flow velocimetry. Time-resolved PIV measurements in water at a framing rate of 2 kHz are presented. The feasibility of LED-based PIV measurements in air is also demonstrated.
Keywords: particle image velocimetry, PIV, light emitting diode, LED, pulsed light source, time-resolved PIV, flow diagnostics, flow visualization
(Some figures in this article are in colour only in the electronic version)

List of symbols

Alum | emitter luminescent area,
f | focal length,
f# | lens aperture (f -number),
If,cw | continuous forward current,
If,max maximum continuous forward current, N.A. numerical aperture,
Pdiss | dissipated power,
λo | dominant emission wavelength,
"v | luminous flux in lumen (lm),
"r | radiometric flux in watt (W),
#t | delay between two illumination pulses (for PIV),

τp | pulse duration,
τrise | rise time.

### 1. Introduction

While earlier generations of LEDs were primarily used as indicators in everyday electronics, recent developments have resulted in mass-produced devices whose light output rivals that of conventional light sources such as incandescent light bulbs and now find an increased range of applications ranging from architectural lighting to projection systems and automotive headlights. In the framework of flow diagnostics, LEDs promise a number of attractive advantages in comparison to lasers and therefore deserve closer investigation. Aside from the dramatically reduced cost of procurement and considerably longer lifetime, an LED provides incoherent light over a rather wide wavelength range (typ. ±10–30 nm) which alleviates many issues related to speckle artifacts found in laser-based illumination. If operated in pulsed mode, the luminosity signal of an LED is extremely stable, both in terms of intensity and spatial intensity distribution. On the other hand the uncollimated nature of the emitted light presents several challenges if the LED is to be used as alternative light source to lasers based in flow diagnostics.

0957-0233/10/075402+11$30.00 | 1 | © 2010 IOP Publishing Ltd Printed in the UK & the USA

Meas. Sci. Technol. 21 (2010) 075402 | C Willert et al
Another interesting characteristic and a main point
of emphasis of the present work is that LEDs can be
operated significantly beyond their damage threshold using
high-current, short duration pulses. In this case, the temperature within the substrate (junction temperature) stays below the damage threshold while the photon generation per time unit is approximately increased in proportion to the current increase [1, 2]. This makes the LED particularly interesting for utilization as a pulsed light source in imagebased diagnostics. The literature reports the use of LEDs in schlieren imaging [3], bubble shadowgraphy [4–6], shadow velocimetry [7], PIV [8] as well as micro-PIV [9]. If operated in a forward scatter shadowgraphy arrangement short duration pulses of τp < 250 ns enable high-speed shadowgraphy in the 100 kHz range of kerosene sprays at high magnification [10]. Short laser as well as LED light pulses can be used as a back illumination for the visualization and recording of the liquid micro-jet disintegration [11, 12]. The present work focuses on side-scatter illumination geometries commonly used in PIV and PTV which require significantly higher illumination intensities.
The following article is arranged in two main parts. The first part deals with the characteristics of high-power LEDs when subjected to pulsed drive currents, including measurements of the increased light flux as a function of drive current, spectral emission characteristics and damage thresholds. The second part investigates the possible use of LEDs in side-scatter imaging configurations both in air and in water flows.

### 2. Overview of high-current LEDs

Table 1 lists the characteristics of several representative LEDs tested in the course of the feasibility study. Mainly green LEDs were investigated, in part because present day imaging sensors exhibit peak quantum efficiencies in the yellow/green range (530 < λo < 550 nm), similar to the response of the human eye. The listed devices represent two different types of LEDs: the first three, available from Philips Lumileds, are designed for general illumination purposes and contain rather small luminous emission chips which are encapsulated in a lensshaped clear dome³. The other two devices, available from Luminus Devices Inc., are specifically designed for projection systems. Here the luminescent substrate is covered by a thin glass window similar to an imaging sensor. Contrary to most commonly available LEDs these devices are essentially surface emitters with a nearly constant intensity distribution per unit area. This is achieved by a photonic lattice attached to the surface of the emitter which channels the light through micron-sized, surface-normal holes. Because of this, the radiation pattern is more collimated than for conventional high-current LEDs.

### 3. LED characteristics in pulsed operation

A central aspect of the current investigation was the pulsed operation of LEDs with a high current over a short duration.

3 At the end of year 2009 Philips Lumileds discontinued the manufacture of the tested LED devices, replacing them with devices of similar performance but different packaging.

Table 1. Specifications of selected high-current LEDs.

If,cw "V | λo | If,max Alum | Pdiss
Emitter | (A) (lm) (nm) (A) | (mm²) | (W)
LXHL-PD09 | 1.4 | 140 627 | 1.54 ≈1.5 × 1.5 | 3
LXHL-PL09 | 1.4 | 110 590 | 1.54 ≈1.5 × 1.5 | 5
LXHL-PM02 | 0.7 | 160 530 | 1.00 ≈2 × 2 | 5
CBT-40 (green) | 5.9 | 625 528 12 | 2.09 × 1.87 25
CBT-120 (green) 18 | 2100 528 36 | 4.6 × 2.6 | 77

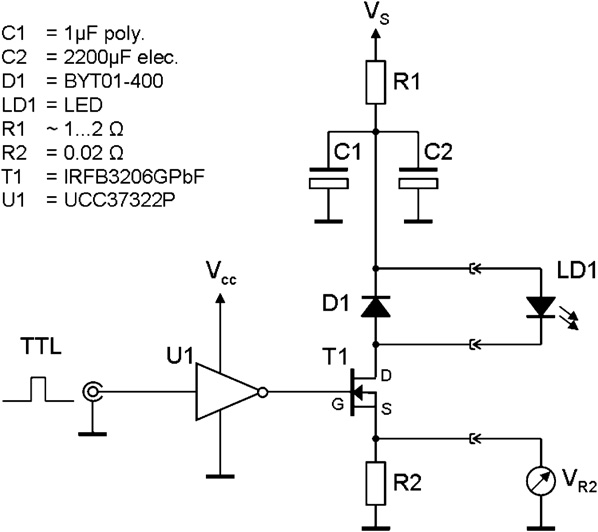
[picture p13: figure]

Figure 1. Example of driver circuit used by the authors for pulsed operation of LEDs.

This was achieved using electronic circuitry which is schematically outlined in figure 1. The operation of the current pulser is very straightforward: a bank of capacitors (C1, C2) with low internal resistance (ESR) is first charged through the power supply VS (typ. 20–50 V). The MOSFET power transistor (T1) is triggered via a MOSFET driver circuit (U1) which has a TTL compatible input. The LED (LD1) cathode is connected to the drain of the power transistor whose source is connected to ground via a low resistance power resistor (R2, typ. 0.01 %–0.1 %). In this configuration the circuit acts as a switched constant-current source for the load, that is, the LED. The voltage drop across this resistor VR2 is used to estimate the current flowing through the LED. Diode D1 protects the LED from potentially damaging reverse currents that arise during the rapid switching transients of the circuit. The purpose of resistor R1 is to limit the charging current of the capacitor bank in between the current pulses and it acts as a rudimentary method of overcurrent protection in case the LED is accidentally operated in continuous mode. Short lead lengths with high cross sections between capacitors C1, C2, transistor T1, diode D1, LED LD1 and ground are essential to obtain good performance. Due to the high pulsed currents and rise times in the microsecond range even short connecting wires result both in significant voltage drops between the electronic components as well as unnecessary inductive loading of the circuit.
The measurements of pulsed LED operation presented in the following sections were performed using both self-designed and commercially available current pulsers. The

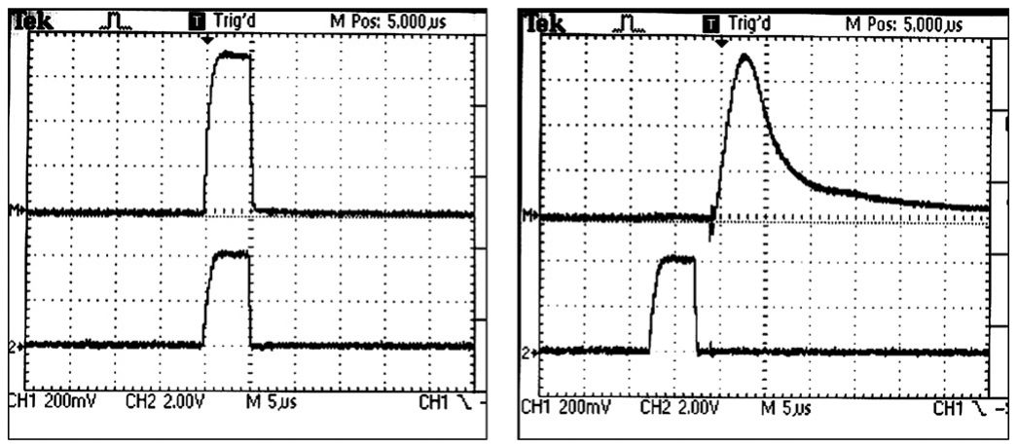
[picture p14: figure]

Figure 2. Time trace of light emission as detected by a photodiode (upper trace) for a high-power LED (left) and a conventional xenon flash lamp (right) in response to a trigger pulse (lower trace).

commercial device (LDP-V 50-100 V3, PicoLAS GmbH) was
specifically designed for the pulsed operation of laser diodes
and is capable of providing current pulses of up to If = 50 A at durations of up to τp = 10 µs with corresponding rise times of τrise ! 4 ns. Due to a limited capacitance available on the supply side of the unit, longer pulses τp > 1 µs exhibit a noticeable exponential decay of the LED drive current and resulted in a corresponding exponential decrease in LED light output during the pulse. This issue was solved with a self-designed driver whose slower rise time (typ. τrise ≈ 100 ns) is acceptable given that the studied range of applications makes use of pulses in the 1 µs < τp < 20 µs range. This circuit is capable of delivering pulsed currents in excess of 200 A using the parts specified in figure 1.
The response of the LED to a current pulse is provided in figure 2(left), where the lower time trace corresponds to the input TTL pulse while the upper is a measurement of the emitted light as detected by a photodiode. Two features are worth remarking in comparison to the response of a conventional xenon flash lamp (EG&G) shown in figure 2(right). First, the duration of the LED light emission can be precisely controlled by the width of the input drive pulse. In contrast, the flash lamp intensity is not correlated with the input pulse modulation and cannot be shortened or lengthened in a simple manner. Second, the rise time of the LED (τrise,LED < 1 µs) is significantly shorter than for the examined flash lamp (τrise,FL ≈ 4 µs). In a similar manner, the decay time of the LED emission strictly follows the drive pulse while the flash lamp’s intensity decays in an exponential fashion over several tens of microseconds. Finally there is no significant lag between the rising edge of input drive pulse and the light flash emitted by the LED while the emission of the flash lamp is delayed by about 8 µs. The reason for this delay is not exactly known and varies from model to model. Figure 3 illustrates the increased luminosity of two high-power LEDs that are driven with short-duration current pulses (here τp = 1 µs at 1 kHz). In both cases the LEDs are driven up to maximum currents in the 30 A range, which is more than a factor 20 higher than the rated forward current If for the red LED. For the green LED the rated current is exceeded

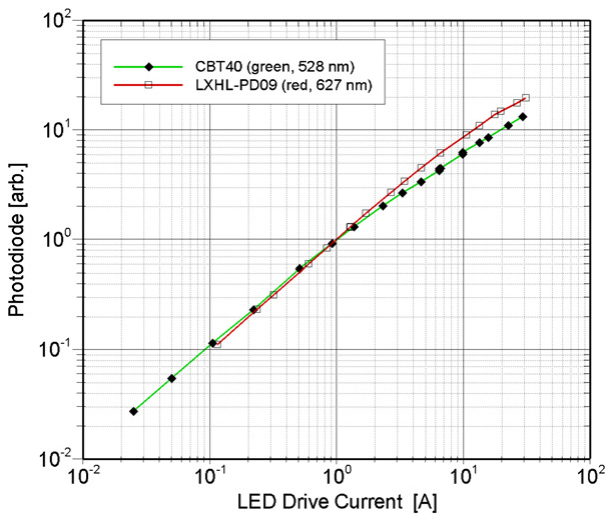
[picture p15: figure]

Figure 3. Luminosity of high-power LEDs (LXHL-PD09, Philips Lumileds; CBT-40, Luminus Devices) driven with 1 kHz current pulses of τp = 1 µs duration.

by a factor of 5, suggesting further increase without damage to the device. In fact none of the tested devices suffered any noticeable damage when operated in pulsed mode at these current levels and low duty cycle (less than 1:100).
The data shown in figure 3 confirm the known increase of luminous flux "v with an increasing drive current If . For the red LED the increase of forward current leads to a proportional increase for low drive currents. At higher currents the efficiency factor or proportionality reduces to about 0.4. The green LED (CBT-40) exhibits a similar behavior for low currents but decreases to about 0.35 at currents beyond If = 10 A. This indicates a decreasing proportionality with increasing drive currents due to saturation effects. Not shown are data for the 5 W green LED (LXHL-PM02) for which the proportionality decreases to 0.2 at currents beyond If = 30 A. In comparison the high-power device CBT-120, which has a three times larger luminescent area than the CBT-40, exhibits a proportionality of 0.47 at If = 40 A, indicating considerable margins for operation at even higher currents. This was confirmed by additional measurements performed on the

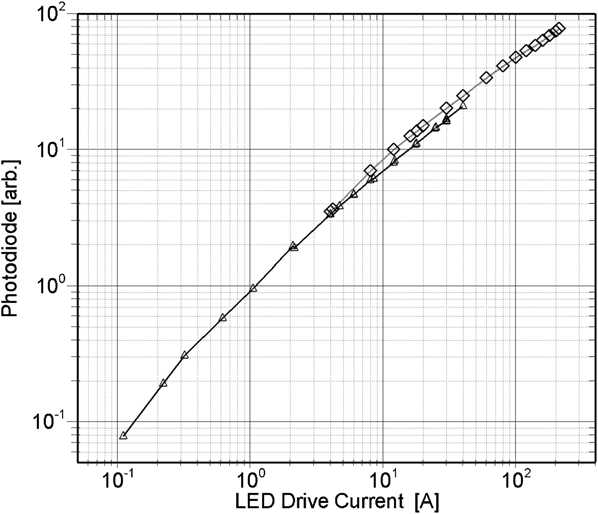
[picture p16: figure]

Figure 4. Luminosity of a high-power green LED (CBT-120, Luminus Devices) driven with current pulses of duration
1 µs at 1 kHz (△) and 10 µs at 25 Hz (⋄).

CBT-120 LED and reproduced in figure 4. The data were obtained using a self-designed driver similar to the one shown in figure 1 capable of delivering τp = 10 µs pulses at a current of up to If = 220 A. Driving this LED at a current of If = 200 A instead of its rated current of If = 18 A increases its light emission by a factor of ∼5.5.
It should be noted that the curves shown in figures 3 and 4 have not been corrected for the wavelength-dependent response of the detector photodiode (Thorlabs, PDA10A). As will be described in the following section the green LEDs have a tendency of emitting shorter wavelength light when subjected to increasing forward currents. Since the photodiode’s responsivity decreases toward the blue–green spectral range the relative luminuous flux for the green LEDs may actually be higher than the measured values presented in figures 3 and 4. On the other hand, most CCD and CMOS camera sensors also have reduced responsivity in this spectral range, such that these measurements are representative of the relative signal gain at the image sensor level when overdriving LEDs.
Measurements of the type shown in figures 3 and 4 allow an approximate extrapolation of luminous flux (or effective pulse energy) at even higher currents. The smaller high-current devices LXHL-PD09 (red) and LXHL-PM02 (green) could be driven at pulsed currents of 50 A without immediate damage, exceeding the rated current by a factor of 30 and 70, respectively. This suggests that the stronger devices CBT-40 and CBT-120 can be driven at significantly higher currents in the 100–200 A range. The data sheet for the CBT-120 quotes a radiometric flux "r = 6.3W ("v = 3100 lm) when driven at a pulsed current of If = 30 A at 240 Hz and a 50% duty cycle [13]. The effective pulse power then is "r = 12.6W for the duration of the current pulse. Assuming a conservative proportionality of 35% light output increase with respect to increasing current—as indicated in figure 3—this would result in an effective pulse power of close 60 W at If = 200 A drive current. This corresponds to a pulse energy of 60 µJ for a

1 µs pulse. As will be demonstrated later this is sufficient to perform reliable high-speed PIV measurements in water.

3.1. Spectral characteristics
A side effect of the pulsed operation of LEDs is that the emission wavelength may shift considerably as the current is increased, generally toward shorter wavelengths. This effect is shown in figure 5 for two LED emitters. The drive pulses are approximately chosen to be of similar integral input power to maintain an average junction temperature. While the amber LED (LXHL-PL09) shows only a minor frequency shift of about #λ = 2 nm toward longer wavelengths, the green device (CBT-40) shifts by more than #λ = 30 nm toward a cyan color. The effect is characteristic for the respective junction materials that the devices are made of, typically GaAsP or AlInGaP for the red and orange luminescence and InGaN for the green and blue LEDs [14]. The spectral width increases slightly for both devices as the drive current increases. In general, the green device has a much wider emission spectrum which is also attributed to the junction material (so-called alloy broadening [14]). While the frequency shift may not be an issue for many velocimetry applications it nonetheless may be of interest when color-selective cameras or filters are used. Wavelength variations may also influence measurements of fluorescence.
3.2. Damage thresholds
After irreversibly damaging several devices in the early stages of this investigation a systematic study was performed to determine the safe operating envelope of the LED used most frequently by the authors (CBT-120, green). This was achieved by fixing the forward pulse current If on the diode and gradually increasing the pulse width until the LED failed. In all cases the LEDs failed due to melting of the bond wires connecting the anode side of the die to the supply line. The measurement results are plotted in figure 6 and were obtained for a pulsing frequency of 25 Hz. Data on previously observed failures have been included (e.g., 2 µs at 350 A). The safe operating envelope—indicated as a dotted line—exhibits three main operation regimes. For pulse widths below 5 µs the maximum pulse current is limited to If ≈ 250 A. For pulse widths in the range 5 µs < τp < 200 µs the damage threshold exhibits a log–linear trend. For pulses τp " 200 µs the damage threshold is in agreement with the maximum current rating of If,max = 36 A provided in the data sheet for the device [13] and shown as a dashed line in figure 6.
The maximum pulsed current limit of 250 A suggests that the bonding wires fail immediately much like a conventional fuse. In the intermediate range for pulse widths of 5 µs < τp < 200 µs the heating of the die due to high current fluxes is believed to additionally heat the bonding wires, which raises their resistance and limits the maximum sustainable current. This seems to be supported by the fact that all bonding wires were melted on the die side of the connection, leaving the supply side unaffected. LEDs damaged due to short current pulses exhibit bonding wires that are nearly completely melted with significant deposits on the front cover

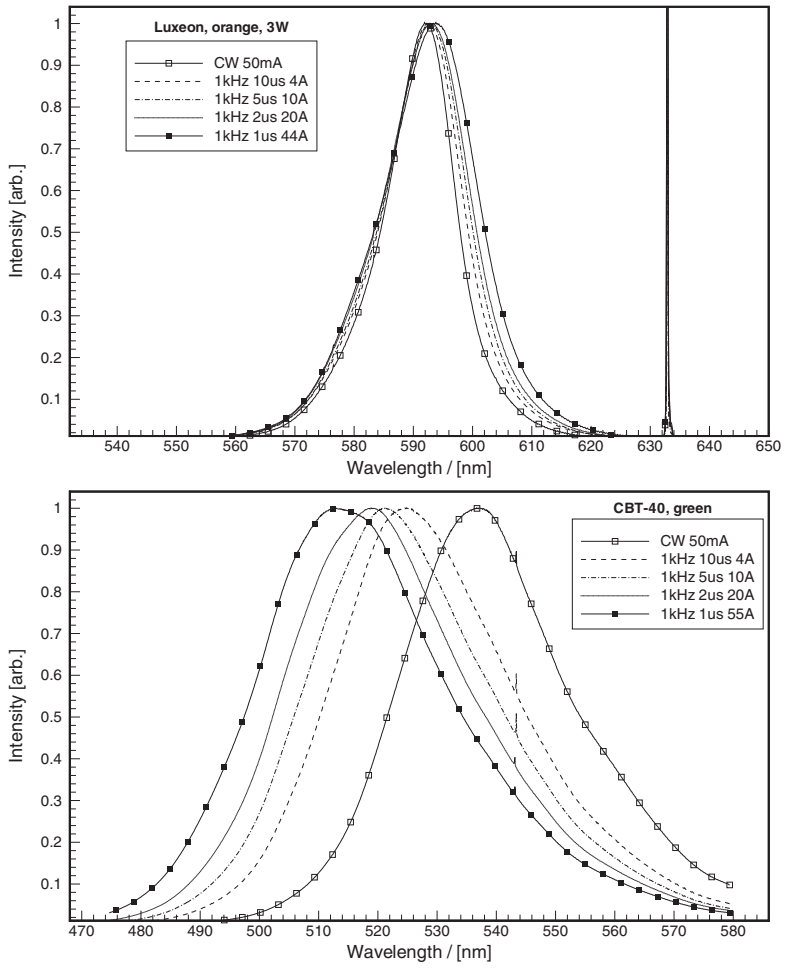
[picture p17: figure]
Wavelength / [nm]; Intensity [arb.]; CW 50mA 1kHz 10us 4A 1kHz 5us 10A 1kHz 2us 20A 1kHz 1us 44A; Luxeon, orange, 3W; CW 50mA 1kHz 10us 4A 1kHz 5us 10A 1kHz 2us 20A 1kHz 1us 55A; CBT-40, green

Figure 5. Spectral intensity distribution of LEDs operating in continuous and pulse modes. Top: LXHL-PL09 (amber); bottom: CBT-40 (green).

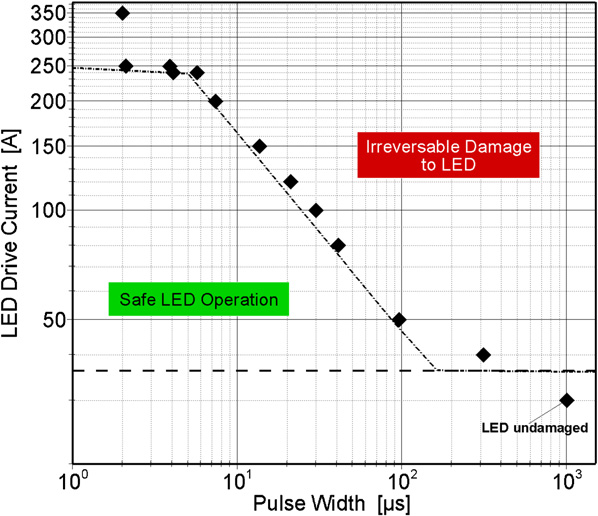
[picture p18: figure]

Figure 6. Experimentally obtained pulsed current damage threshold for a CBT-120 (green) LED. The dashed horizontal line indicates the maximum rated forward current (36 A) quoted in the device’s data sheet.

glass window.For pulse widths τp > 200 µs the LED will fail due to thermal damage in the die itself, typically at internal junction temperatures exceeding 150 ◦C. These observations suggest that thicker or more bonding wires may actually allow the diode to withstand even higher, short-duration pulsed currents. This seems supported by the fact that the Luxeon devices (LXHL-PM02, LXHL-PL09) sustained continuous 1 kHz pulses of τp = 1 µs at forward currents If " 40 A which is more than 50 times the rated current for the LXHL-PM02 device. In comparison, the CBT-120 devices failed at about 14 times the rated continuous forward current. Another possible cause for LED damage is too short a rise time of the pulse current. Even though the LED can withstand a continuous train of 200 A pulses of τp = 7.5 µs with rise times of about τrise ≈ 1 µs, it will be immediately damaged when the rise time is shortened below 0.5 µs. The data sheet for the device also recommends rise times of greater than 0.5 µs from 10% to 90% of forward current [13]. While the devices can be damaged due to excessive current overdriving, increased ageing is likely to occur, resulting in

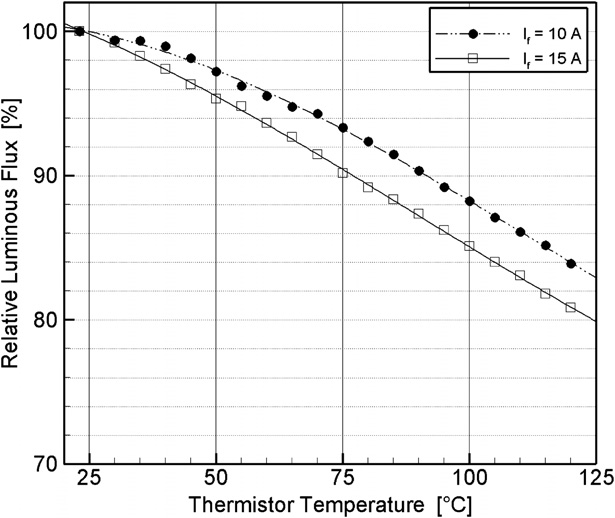
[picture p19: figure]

Figure 7. Luminous flux versus die temperature for a CBT-120 (green) LED running in CW mode (If = 15 A, Pdiss = 93 W).

a gradual reduction of light emission, but this has not been noticed or investigated by the authors. Driving the LEDs at high currents briefly increases the junction temperature which strains the crystal, causing defects in its lattice which then no longer contribute to light generation. With increasing temperatures the luminous flux from the LED also decreases such that active cooling can in fact both increase the light output (figure 7) as well as increase the lifetime of the LED itself. A convenient way of cooling the LED is offered through the use of commercially available cooling assemblies for personal computer CPUs along with copper plate to function as a heat spreader between LED and heat sink.

### 4. PIV using LED

As mentioned in section 1, the literature reports a number of earlier PIV applications involving LED clusters as light sources [4, 5, 7–9]. In these applications the LEDs were rarely overdriven to levels reported here and generally were

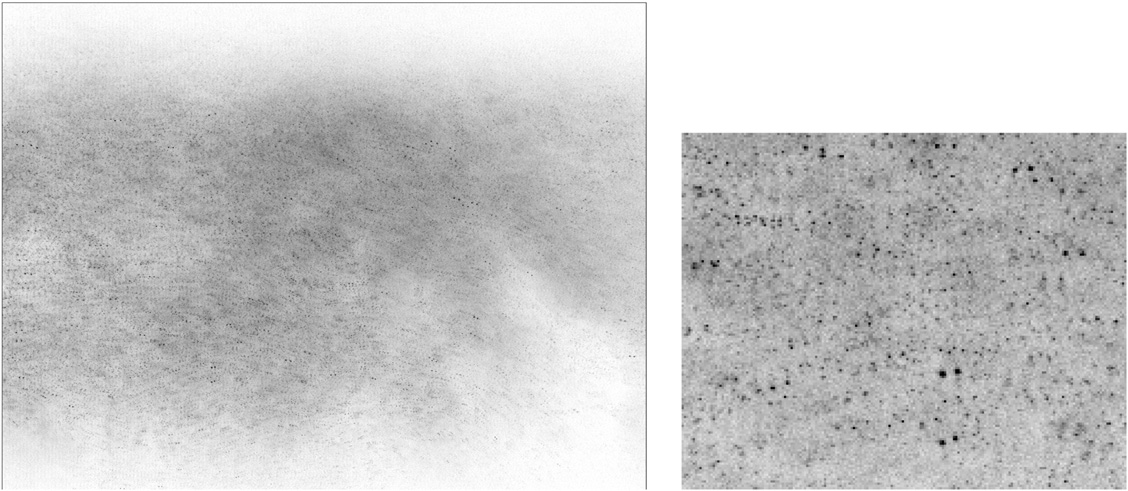
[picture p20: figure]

Figure 8. PIV recording of an air flow obtained with LED illumination in forward scatter shown with inverted intensity scale (black = bright). Magnified sub-region of image to the left (area ≈ 1.5 × 1.2 mm²) (right).

operated in an in-line imaging arrangement or relied on large particles to achieve sufficient light scattering.
The present LED–PIV investigations focused on using single LEDs to illuminate particles in a side-scatter arrangement which is commonly used in planar PIV. Initially volume illumination was used in which the luminescent area of the LED is projected into the flow under investigation using condenser lenses. A combination of high magnification and large lens aperture limited the depth of field in the sub-millimeter regime and permitted two-component PIV measurements on an area of about 10 × 7.5 mm². A5W class green LED (LXHL-PM02) was pulsed at If = 2 A for τp = 20 µs. PIV measurements were reliable using 10 µm particles in water, imaged by a cooled, double-shutter CCD camera.
4.1. LED–PIV measurements of an air flow
Motivated by the initial PIV measurements in water flows, later PIV experiments made use of stronger, projection type LEDs (CBT-40, CBT-120) that could be driven at much higher currents and due to their larger luminescent areas provided considerably more light per unit time. These devices were used to test the feasibility of imaging micron-sized particles in air. Figure 8 shows a PIV recording imaging a 9.5×7 mm² portion of a free jet in air seeded with 1–3 µm glycerin droplets. Volume illumination was provided by the CBT-120 LED device using 30 A pulses of τp = 2 µs duration. The pulse delay was #t = 15 µs. Arranged in a 45◦ forward scattering with respect to the LED light a macro lens (Nikon Nikkor MF 55 mm/f#2.8) with aperture set at f#4 imaged the flow onto the actively cooled sensor (1376×1040 pixel) of a double-shutter CCD camera (Sensicam QE, PCO AG) using a magnification of approximately 1:1. Assuming a circle of confusion of 5 pixel the depth of field is estimated to be 500 µm. The processed PIV data set shown in figure 9 was analyzed using sampling areas of 48 × 48 pixel (320 × 320 µm²).
While these PIV measurements demonstrate the feasibility of imaging micron-sized droplets in air at moderate

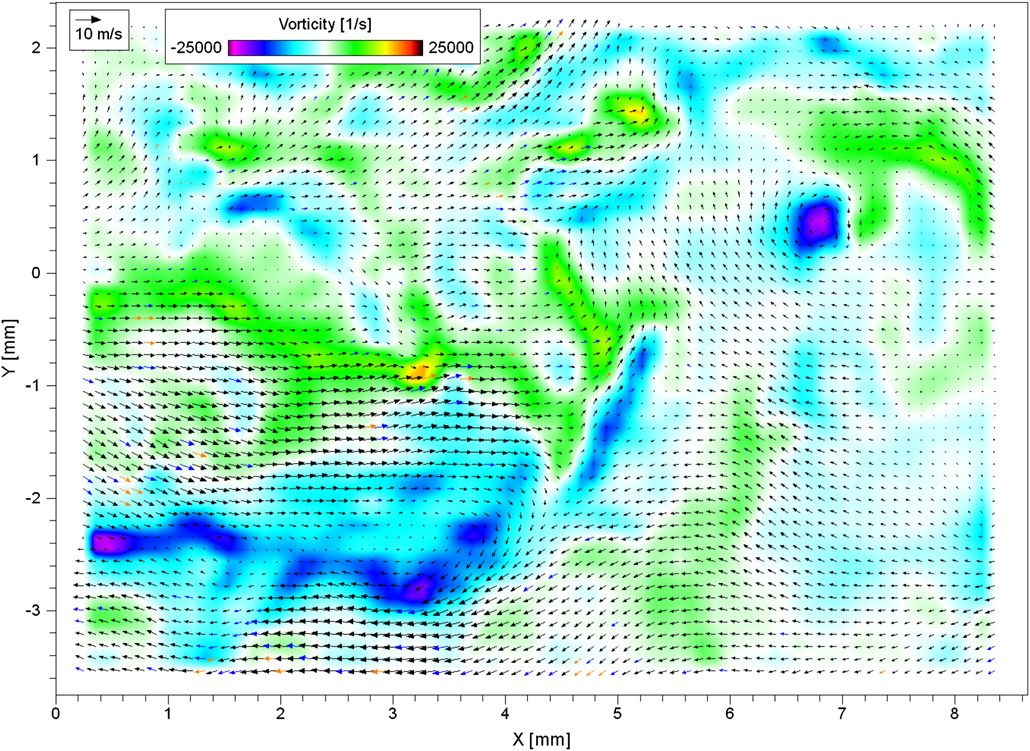
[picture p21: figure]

Figure 9. Processed PIV data set corresponding to figure 8 obtained with LED illumination. For clarity purposes a constant horizontal flow component of about 7 m s−1 has been subtracted. Orange vectors indicate interpolated data, and blue vectors are displacement data obtained from lower order correlation peaks.

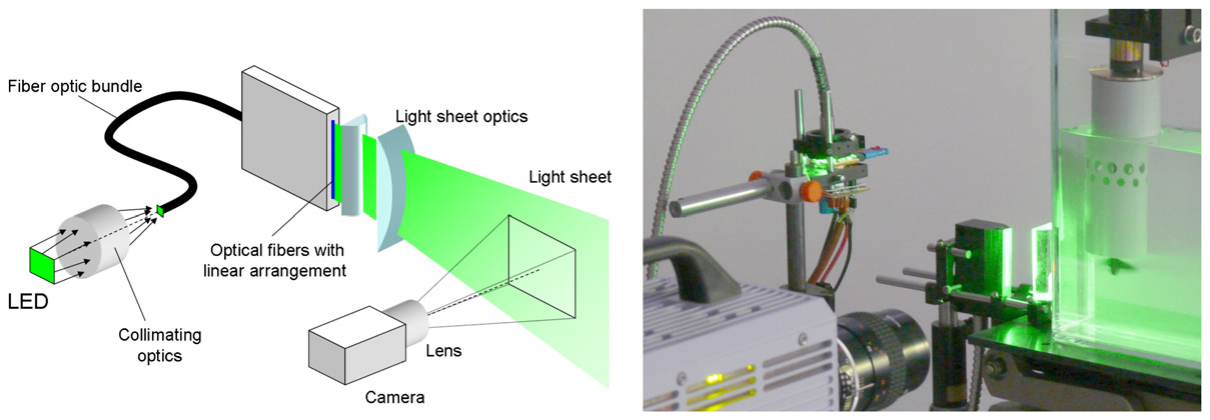
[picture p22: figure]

Figure 10. Schematic of LED-based light sheet illumination using a fiber optic line-light assembly (left). Photograph of a high frame rate LED–PIV setup on a small propeller in water (right).

velocities using rather short illumination pulses, the method
of volume illumination has the drawback of introducing significant background signal due to the light scattered by out-of-focus particles. This reduces image contrast and poses a common problem for PIV applications in general. Therefore possibilities of converting the highly divergent light of the LEDs into a light sheet were investigated in a further iteration.
4.2. LED–PIV measurements of a water flow
The most promising experiments were performed when the LED light was bundled into a light sheet by means of a fiberoptic illumination system, also known as line light (e.g., Dolan-Jenner Industries, Model QF2036). As illustrated in figure 10 the entry side of the fiber bundle is round (3 mm diameter) while the fibers at the distal end are arranged along a straight line of 38 mm height and 0.5 mm thickness. A light sheet can then be formed by projecting this line into the area under investigation using a short focal length cylindrical lens (here f = 25 mm).
Figure 11 provides a sample PIV result from a time series of the turbulent water flow downstream of a small propeller acquired at a frame rate of 2 kHz using pulsed LED illumination and a high-speed CMOS camera (PCO.DIMAX, PCO AG). Fitted with f = 55 mm f#2.8 lens (Nikon Nikkor MF) the camera’s image magnification was about 40 pixel mm−1. The water was seeded with 10 µm hollow glass spheres (Conduct-o-Fil, Potters Industries Inc.). The light

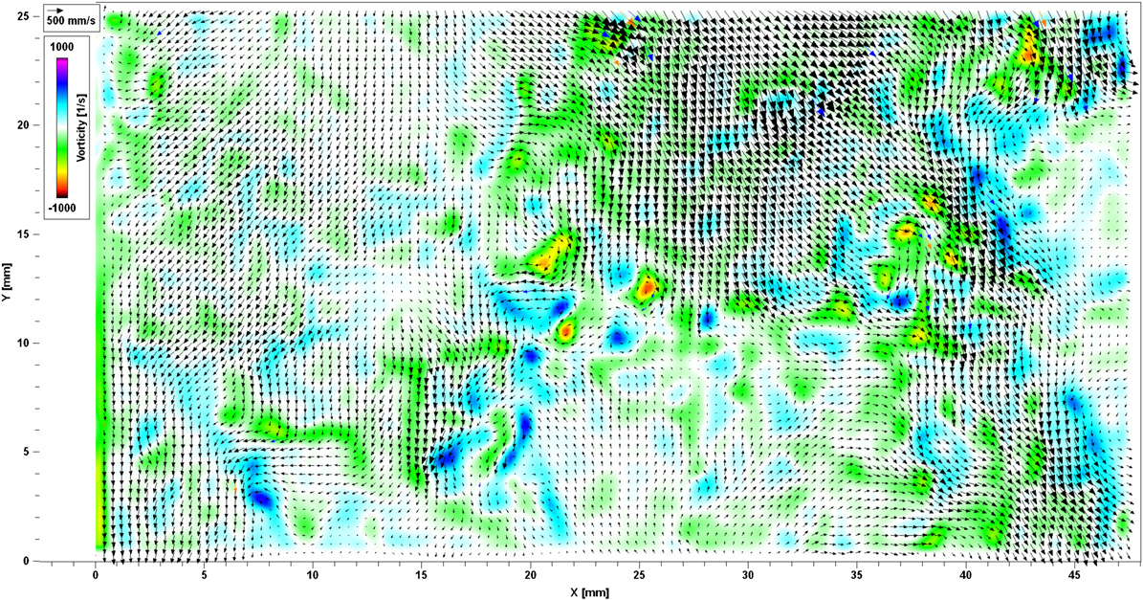
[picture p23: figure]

Figure 11. Single PIV map from a time-resolved image sequence acquired at 2 kHz of the turbulent flow downstream of a propeller inside a small water tank. Blue vectors are obtained from lower order correlation peaks while orange vectors indicate interpolated vectors.

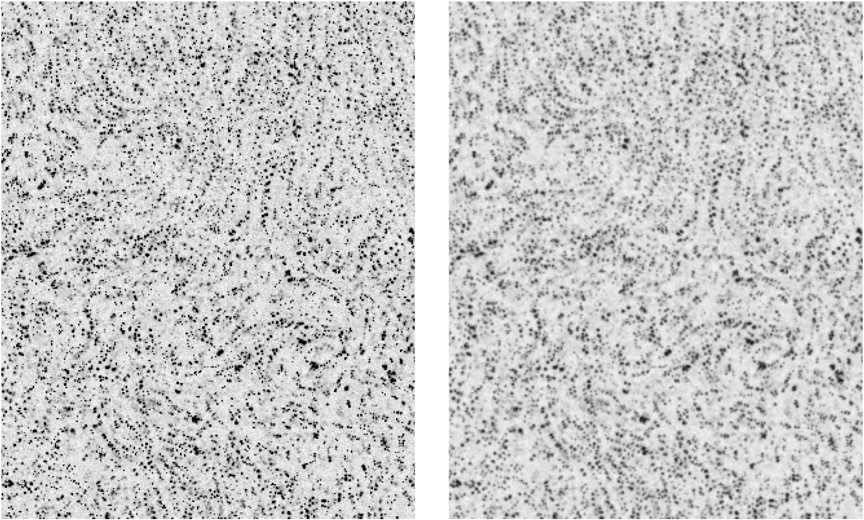
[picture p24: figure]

Figure 12. Detail of overlaid PIV recording image pair of water flow in figure 11 with inverted intensity scale (black = bright) extracted at 20 ! x ! 28 mm, 7 ! y ! 17 mm. Low-pass-filtered version of the image used for PIV analysis (right). Illumination pulse separation is #t = 500 µs.

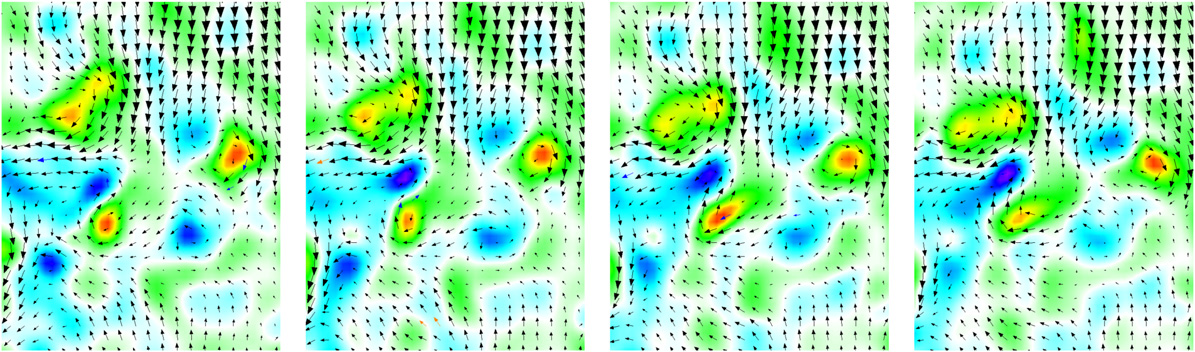
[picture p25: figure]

Figure 13. Four consecutive PIV maps of a selected portion of figure 11. Separation between displayed recordings is 1 ms.

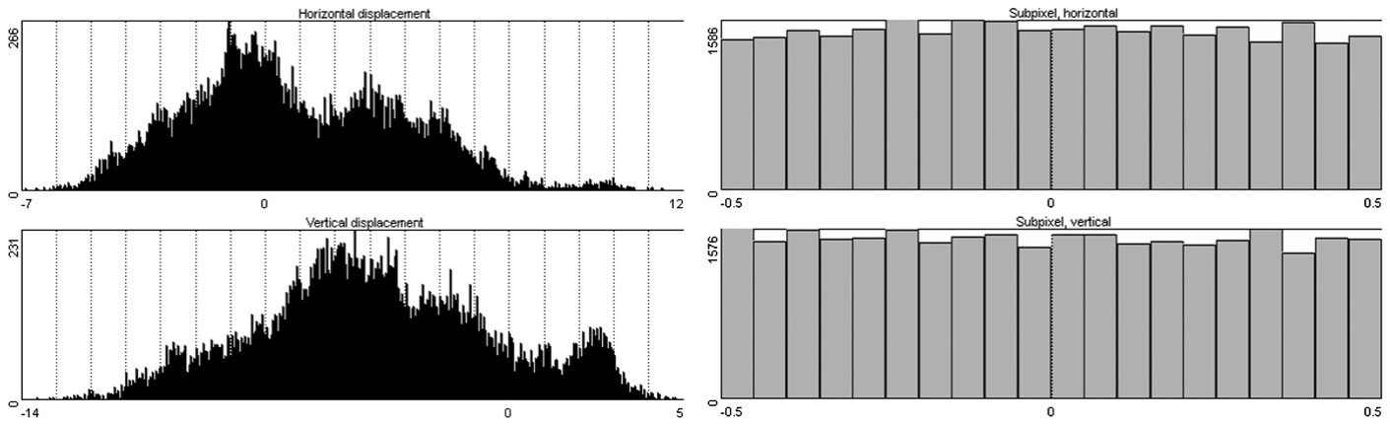
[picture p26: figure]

Figure 14. Histograms of the two displacement components of the data provided in figure 11 (left); histograms of fractional displacements (right).

sheet thickness was approximately 1 mm at the waist widening
to about 2 mm at the edges of the 50 mm wide imaged area.
Current pulses of 50 A and τp = 20 µs duration were used, which is more than a factor of 2 below the damage threshold plotted in figure 6. At these settings the LED driver circuits draw an average current of 2 A at a supply voltage Vs ≈ 12 V. Using information on the LED’s optical power quoted in the data sheet along with the luminous flux increase provided in figure 4, the single pulse energy emitted by the LED is estimated to be about 400 µJ.
Prior to PIV processing the recorded images were subjected to image contrast enhancement involving background subtraction and intensity clipping [15]. Additional smoothing of the image with a small kernel further reduced spurious detector noise [16]. Samples of the image data are given in figure 12 before and after image enhancement. The particle image density was sufficient to sample the images with 16 × 16 pixel sub-windows, corresponding to 0.4×0.4 mm². Since the light sheet thickness is of the order of 1 mm a sample window of 32 × 32 pixel was chosen which corresponds to a roughly cubic sampling volume. With these settings the data yield was close to 100% with about 10–20 spurious vectors per PIV recording consisting of about 7400 vectors. A sequence of an enlarged region of the time-resolved PIV data near x = 20 mm, y = 10 mm is shown in figure 13. Each of the image pairs has been processed individually, that is there is no frame-to-frame averaging of the recovered velocity data. Histograms of the recovered displacement data show no signs of peak locking (figure 14).

### 5. Discussion

The previously described experiments clearly demonstrate the viability of using pulsed, high-power LEDs as illumination sources for PIV in classical side-scatter imaging configurations. Generally being an uncollimated light source is one of the more critical drawbacks of the LED. This makes it difficult to establish light sheet illumination commonly found in macroscopic PIV applications unless additional optics such as the fiber optic line lights are used. Unfortunately the large aperture of the typically Lambertian radiative pattern of LEDs (N.A. ∼ 1) does not match well to the smaller aperture of optical fibers (typ. N.A. ≈ 0.55), such that a significant amount of light is lost. Comparable measurements between volume illumination and light sheet illumination indicated that up to three quarters of the light is lost by the fiber transmission system. Suitable collimation devices are the subject of ongoing investigations. Nonetheless fiber optic line lights with multiple proximal fiber bundle branches are commercially available and allow the light output to be increased proportionally. The collimating optics for the light sheet can be improved by replacing the plane convex lens of the current setup with a best form lens which reduces the halo around the light sheet.
Collimation is of lesser importance when LEDs are used to provide volume illumination, for instance in microscopic PIV or photogrammetric particle imaging methods such as tomographic PIV or 3D particle tracking. The herein reported PIV measurements of an air flow involved volume illumination in a forward scattering arrangement with the depth of volume defined by the large aperture lens. Due to the small particle size the signal recorded by the camera is rather low. Due to driver limitations these measurements were performed at a rather low drive current of If = 30 A which, based on the data in figure 6, could have increased to If ≈ 200 A providing about four times more light. At present, LED– PIV measurements of water flows seem more viable since larger particles in the 10 µm range can be used. Successful tomographic PIV measurements of grid turbulence in a water channel have been performed by the authors but are beyond the scope of this paper and will be published in the future. Due to the quasi-continuous illumination of the flow during the LED pulse, the pulse separation between the two exposures comprising a PIV recording has to be properly matched to avoid streaking. The air flow measurements presented in section 4.1 had a duty cycle of about 13% (2 µs pulses with 15 µs separation), which means that for displacements of 15 pixels the streaking is 2 pixels. This is of the same order as the optimum particle image diameter. The self-similarity of the resulting particle image will result in a slightly elongated correlation peak in the direction of the displacement vector (ignoring curvature and acceleration effects).
The time-resolved water flow measurements in section 4.2 were acquired at a much smaller duty cycle of 4% (20 µs pulses with 500 µs period) with which flow speeds in excess of 0.5ms−1 (10 pixel displacement) could be measured reliably in a 50×50 mm² field of view. A further increase of the duty cycle to 10% would allow measurements up to ≈1.5ms−1 at this magnification without reducing the illumination pulse width.

### 6. Conclusions

The use of LED-based illumination for flow measurement was investigated as a possible alternative to commonly used laser-based illumination. The study was motivated by the recent availability of high-power LEDs with continuous radiant flux levels comparable to that of lasers. Pulsed light at significant intensity levels can be obtained from these solid state devices by briefly overdriving them with high currents. The emitted light was sufficient for PIV measurements in both water and air.
Challenges yet to be solved are associated with the rather wide-angle radiation pattern (i.e., high N.A.) of the light issuing from the luminous surface of the LED. The high numerical aperture restricts the creation of thin light sheets comparable to those achieved with the collimated light of lasers. Nonetheless, reasonable light sheets can be achieved using a fiber optic collimating device with which time-resolved PIV measurements were performed in water at frame rates exceeding 4 kHz.
PIV systems using LEDs as light sources can be assembled at significantly reduced costs. The combined cost of LED light source, driver unit components and fiber optics used in the high-speed imaging setup amount to roughly 500.00 Euro. Compact, battery operated systems are feasible and could be of interest for in-flight measurements or autonomous operation in hazardous environments. From a handling point of view the uncollimated light of LEDs is less dangerous, but not necessarily eye-safe, while supply voltages are considerably lower than for pulsed lasers.
In comparison to pulsed lasers commonly used for PIV, which require a pre-trigger time of the order of 100 to 300 µs to pump the lasing medium, the light pulses of LEDs can be ‘fired’ with insignificant delay, that is, within several nanoseconds, depending on the support electronics. The rise time of LEDs is in the 100 ns range. The pulse repetition rate can be freely varied since LEDs do not need to be operated at specific pulsing frequencies. Pulseto-pulse intensity and spatial variations are practically not present. The broad spectral intensity distribution of the LED’s electroluminescence prevents the creation of speckle (interference of coherent light).
Future developments will undoubtedly lead to LEDs with even higher light output per surface area. The high-power devices used for the present investigations had a luminous output of the order 175 lm per square millimeter of die area (0.3 W mm−2) at a luminous efficacy around 20–30 lm per watt of input power. Luminous efficiencies in excess of 100 lm W−1 have already been demonstrated for high-power, white light LEDs. Current technology trends will likely result in LED devices that are suitable light sources for flow diagnostics, in particular for planar techniques as well as the recently introduced volume-resolving, particlebased velocimetry techniques (e.g., tomographic PIV [17] or 3D-PTV [18]). Currently available high-power LEDs are also particularly well suited for applications requiring volume illumination such as shadowgraphy and high-speed schlieren imaging. Beyond the flow imaging applications presented here the use of pulsed LED illumination is also very attractive in high-speed imaging of fast moving objects.

Acknowledgments

This work was partly funded by the German Ministry of Education and Research (BMBF), PTJ Research Project number 03FPE00003. This support is gratefully acknowledged by the authors.

References

[1] Hiller W, Lent H M, Meier G E A and Stasicki B 1987 A pulsed light generator for high-speed photography Exp. Fluids 5 141–4 (http://dx.doi.org/10.1007/BF00776185)
[2] Stasicki B, Hiller W and Meier G E A 1984 Hochfrequenz-Stroboskop mit LED-Lichtquelle Tech. Mess. 51 217–20
[3] Buttsworth D and Ahfock T L 2003 A pulsed LED system for Schlieren flow visualization Tech. Rep. TR-2003-01 (University of Southern Queensland, Australia)
[4] Broder D and Sommerfeld M 2007 Planar shadow image ¨ velocimetry for the analysis of the hydrodynamics in bubbly flows Meas. Sci. Technol. 18 2513–28 (http://dx.doi.org/10.1088/0957-0233/18/8/028)
[5] Lindken R and Merzkirch W 2002 A novel PIV technique for measurements in multiphase flows and its application to two-phase bubbly flows Exp. Fluids 33 814–25
[6] Nogueira S, Sousa R, Pinto A, Riethmuller M and Campos J 2003 Simultaneous PIV and pulsed shadow technique in slug flow: a solution for optical problems Exp. Fluids
35 598–609 (http://dx.doi.org/10.1007/s00348-003-0708-8)
[7] Estevadeordal J and Goss L 2005 PIV with LED: Particle Shadow Velocimetry (PSV) technique 43rd AIAA Aerospace Sciences Meeting and Exhibit (Reno, NV)
[8] Chetelat O and Kim K C 2002 Miniature particle image ´ velocimetry system with LED in-line illumination Meas. Sci. Technol. 13 1006–13 (http://dx.doi.org/10.1088/0957-0233/13/7/306)
[9] Hagsater S M, Westergaard C H, Bruus H and Kutter J P 2003 ¨ Investigations on LED illumination for micro-PIV including a novel front-lit configuration Exp. Fluids 44 211–9
[10] Willert C, Freitag S and Hassa C 2008 High speed imaging of fuel sprays using a low-cost illumination source 22nd European Conf. on Liquid Atomization and Spray Systems (ILASS 2008)
[11] Charvat A, Stasicki B and Abel B 2006 Product screening of fast reactions in IR-laser-heated liquid water filaments in vacuum by mass spectrometry J. Phys. Chem. A
110 3297–306 (http://dx.doi.org/10.1021/jp055165e)
[12] Stasicki B, Abel B, Charvat A and Faubel M 2005 Visualization of laser-induced liquid micro-jet disintegration by means of high-speed video stroboscope 26th Int. Congr. on High Speed Photography and Photonics

(Alexandria, VA, USA), Proc. SPIE vol 5580,
ed D L Paisley, S Kleinfelder, D R Snyder and
B J Thompson pp 335–46
[13] Luminus Devices Inc. 2008 Technical Product Data Sheet PDS-001226: CBT-120 Series, PhlatLight LED Illumination Products
[14] Saleh B and Teich M 2007 Fundamental of Photonics 2nd edn (Hoboken, NJ: Wiley)
[15] Shavit U, Lowe R J and Steinbuck J V 2007 Intensity capping: a simple method to improve cross-correlation PIV results Exp. Fluids 42 225–40
[16] Raffel M, Willert C E, Wereley S T and Kompenhans J 2007 Particle Image Velocimetry—A Practical Guide 2nd edn (Berlin: Springer)
[17] Elsinga G, Scarano F, Wieneke B and van Oudheusden B 2006 Tomographic particle image velocimetry Exp. Fluids
41 933–47
[18] Pereira F, Gharib M, Dabiri D and Modarress D 2000 Defocusing digital particle image velocimetry: a 3-component 3-dimensional DPIV measurement technique: application to bubbly flows Exp. Fluids

### 29 S078–84

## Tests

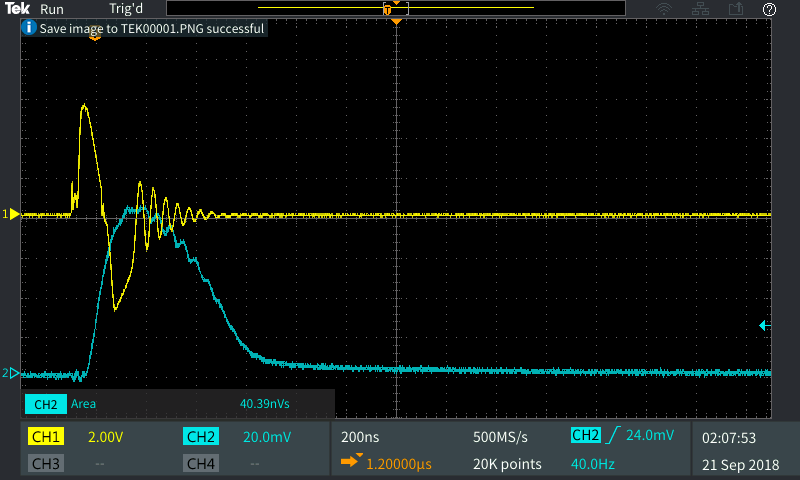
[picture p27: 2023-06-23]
Pictures/Photodiode Measurements/100ns.PNG

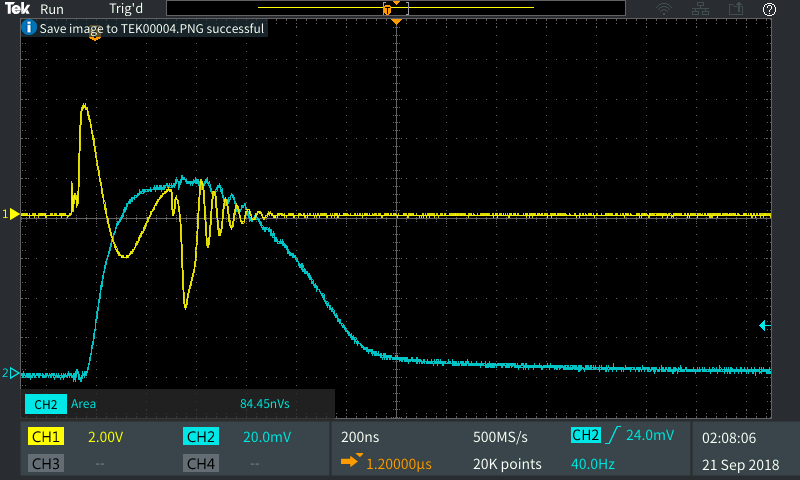
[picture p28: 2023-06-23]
Pictures/Photodiode Measurements/400ns.PNG

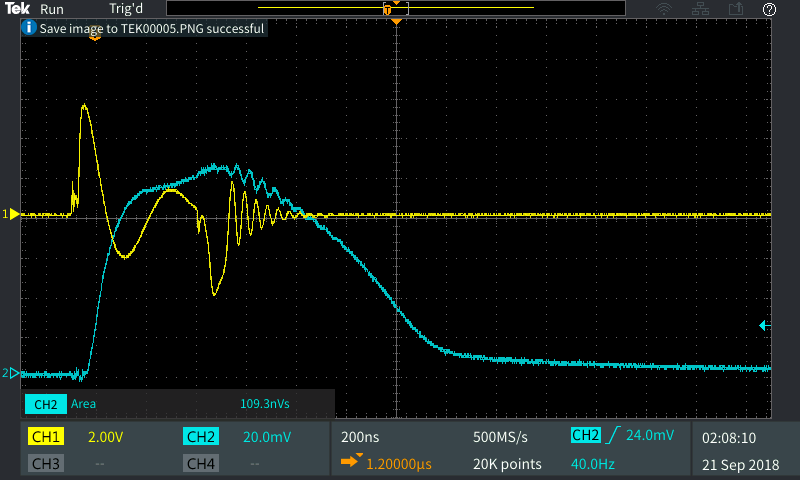
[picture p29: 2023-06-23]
Pictures/Photodiode Measurements/500ns.PNG

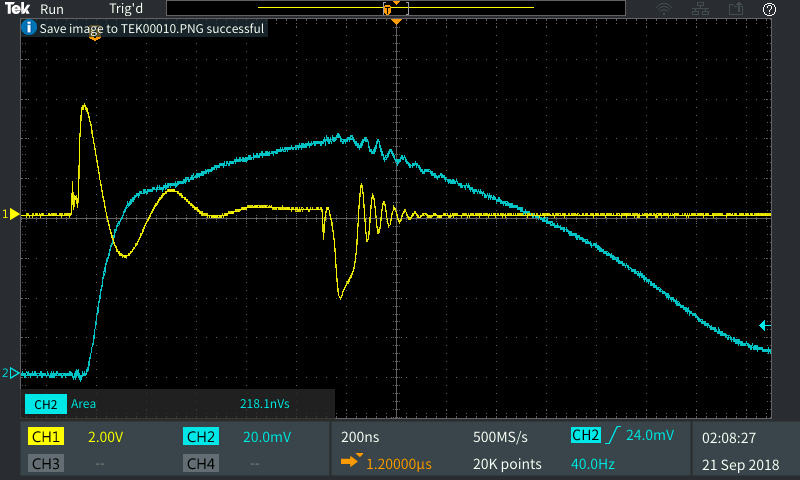
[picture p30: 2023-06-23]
Pictures/Photodiode Measurements/1000ns.PNG

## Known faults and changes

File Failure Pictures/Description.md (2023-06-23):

This is how the LED bond wires fail when the LED is overdriven. Hope you won't have your LED's do that!

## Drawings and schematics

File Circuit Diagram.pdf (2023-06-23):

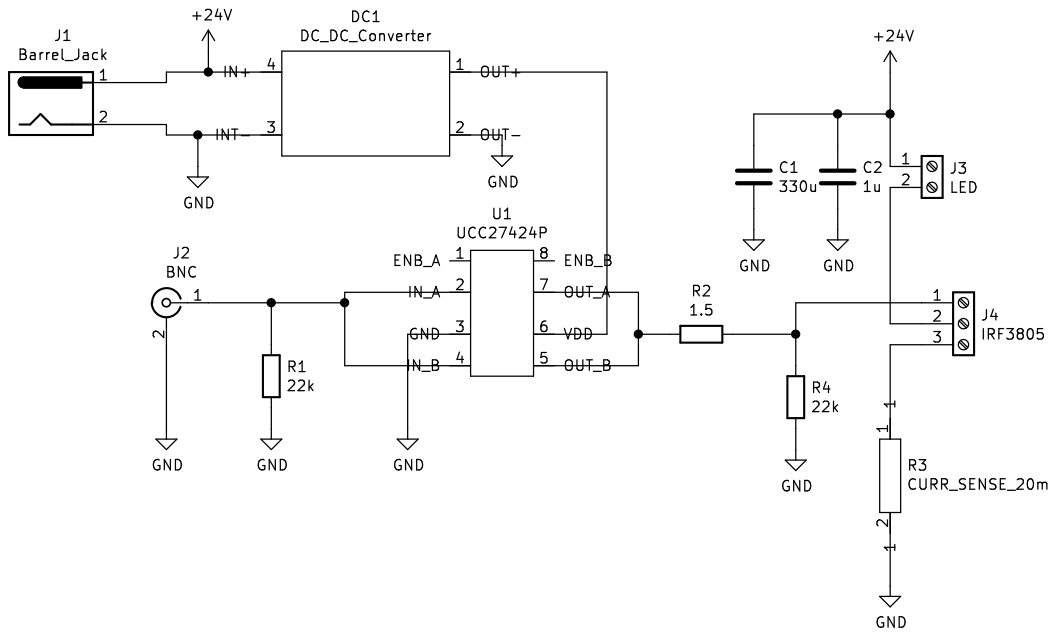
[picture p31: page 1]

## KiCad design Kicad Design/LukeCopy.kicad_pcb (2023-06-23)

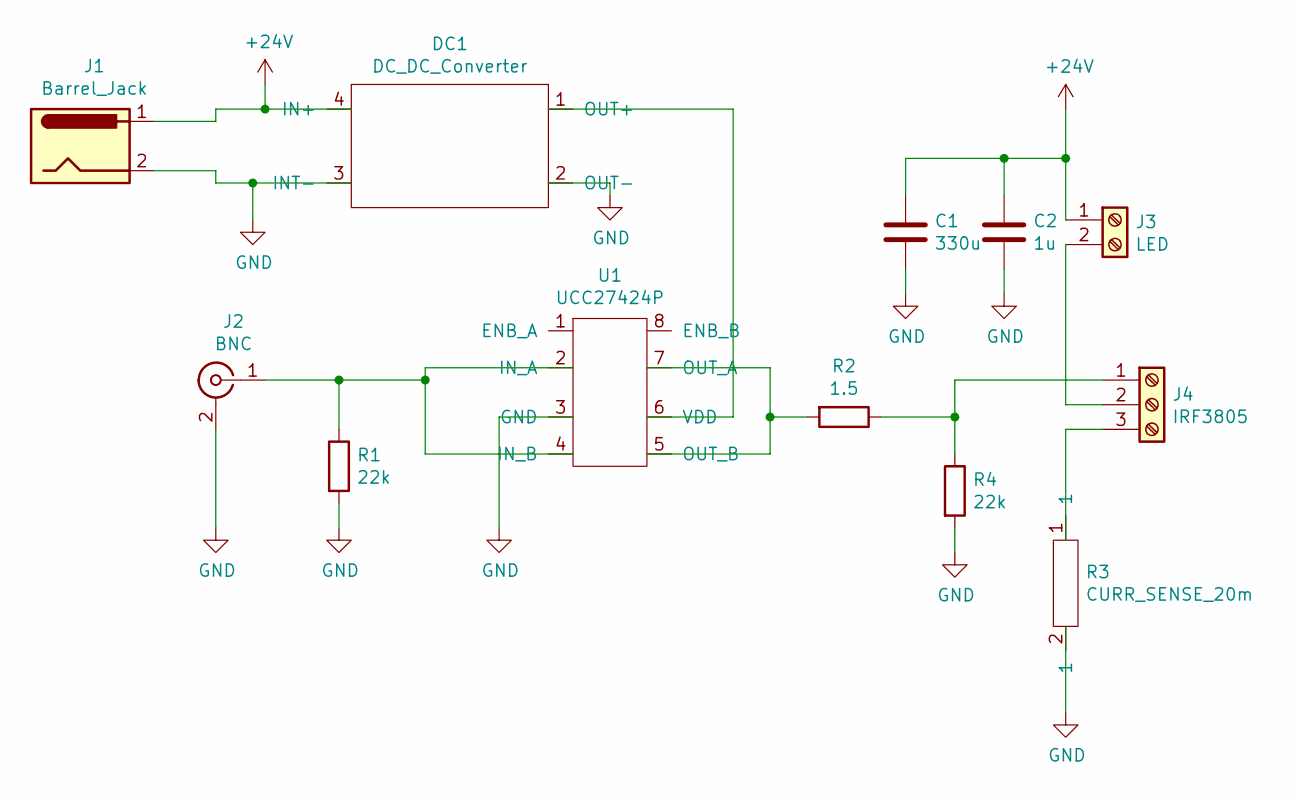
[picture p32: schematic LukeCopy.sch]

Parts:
C1: 330u; CP_Radial_D5.0mm_P2.50mm
C2: 1u; C_Disc_D5.1mm_W3.2mm_P5.00mm
DC1: DC_DC_Converter; DCDC_Converter
J1: Barrel_Jack; BarrelJack_Horizontal
J2: BNC; BNC_Connector
J3: LED; TerminalBlock_bornier-2_P5.08mm
J4: IRF3805; TerminalBlock_bornier-3_P5.08mm
R1, R4: 22k; R_Axial_DIN0204_L3.6mm_D1.6mm_P7.62mm_Horizontal
R2: 1.5; R_Axial_DIN0207_L6.3mm_D2.5mm_P10.16mm_Horizontal
R3: CURR_SENSE_20m; CurrentSenseResistor
U1: UCC27424P; DIP-8_W7.62mm

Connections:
+24V: C1.1, C2.1, DC1.4 (IN+), J1.1, J3.1
GND: C1.2, C2.2, DC1.2 (OUT-), DC1.3 (INT-), J1.2, J2.2 (Ext), R1.2, R3.2, R4.2, U1.3 (GND)
unnamed: DC1.1 (OUT+), U1.6 (VDD)
unnamed: J2.1 (In), R1.1, U1.2 (IN_A), U1.4 (IN_B)
unnamed: J3.2, J4.2
unnamed: J4.1, R2.1, R4.1
unnamed: J4.3, R3.1
unnamed: R2.2, U1.5 (OUT_B), U1.7 (OUT_A)

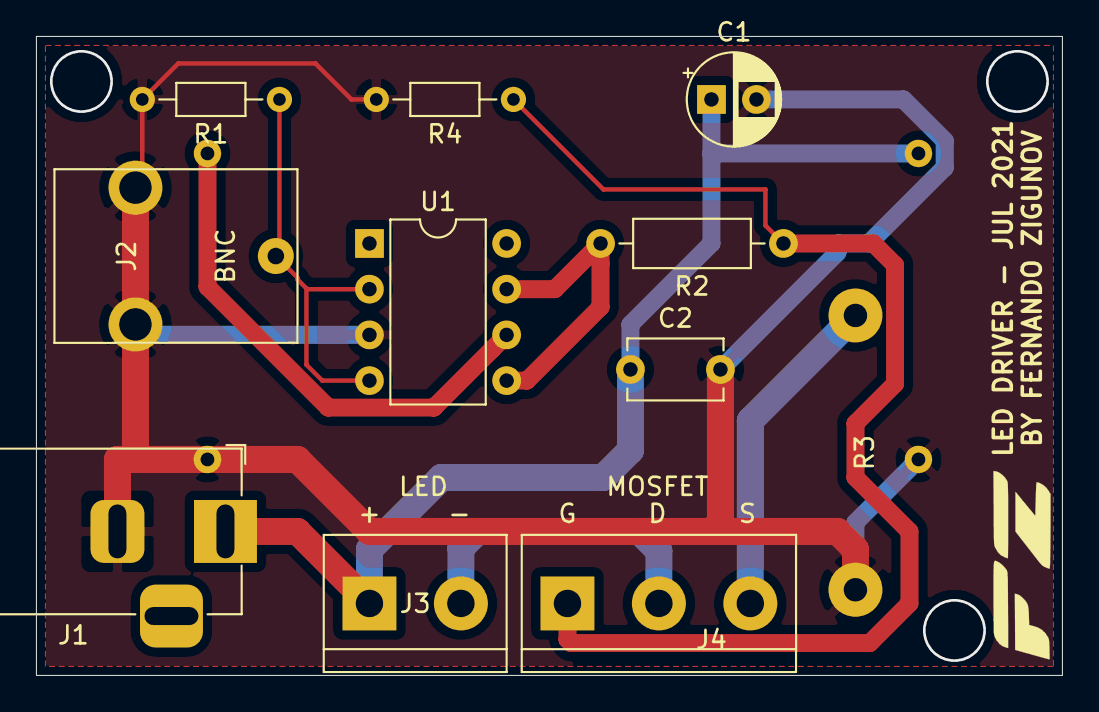
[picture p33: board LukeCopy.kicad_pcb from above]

Board: 2 copper layers, 57.0 x 35.5 mm, 12 parts (1 on the bottom side), 8 nets.
